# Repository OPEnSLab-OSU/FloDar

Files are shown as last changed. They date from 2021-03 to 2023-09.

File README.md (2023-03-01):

# FloDar | [Updates](https://github.com/OPEnSLab-OSU/OPEnS-Lab-Home/wiki/FloDar-updates) | [Wiki](https://github.com/OPEnSLab-OSU/OPEnS-Lab-Home/wiki/FloDar)

Project Lead: Cara Walter

This repository contains software, hardware, and documentation for FloDar.

See our [Wiki](https://github.com/OPEnSLab-OSU/OPEnS-Lab-Home/wiki/FloDar) for more information!

Project contact: Cara Walter (cara.walter@oregonstate.edu)

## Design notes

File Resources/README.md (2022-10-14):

# FloDar Resources

This directory is for holding diagrams, images, or other forms of documentation that may be referenced by our [Wiki](https://github.com/OPEnSLab-OSU/OPEnS-Lab-Home/wiki/FloDar) or elsewhere.

## System Diagram

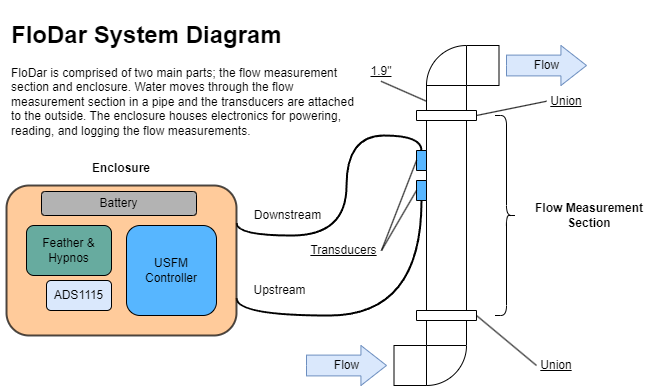
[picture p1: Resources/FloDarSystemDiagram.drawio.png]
FloDarSystemDiagram


## Circuit Diagram

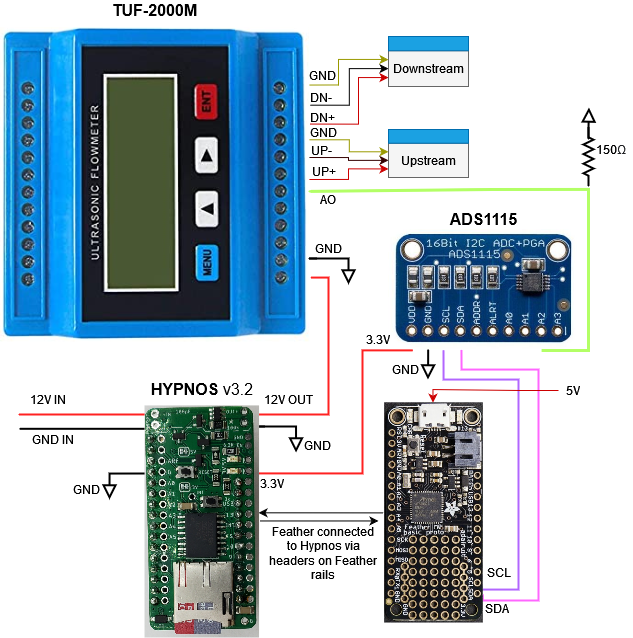
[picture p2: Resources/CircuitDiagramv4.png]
CircuitDiagram


## Black Box Diagram
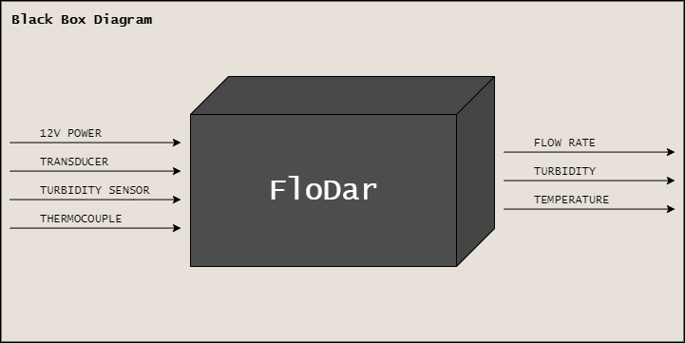
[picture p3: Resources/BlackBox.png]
Black Box Diagram


## FloDar Render
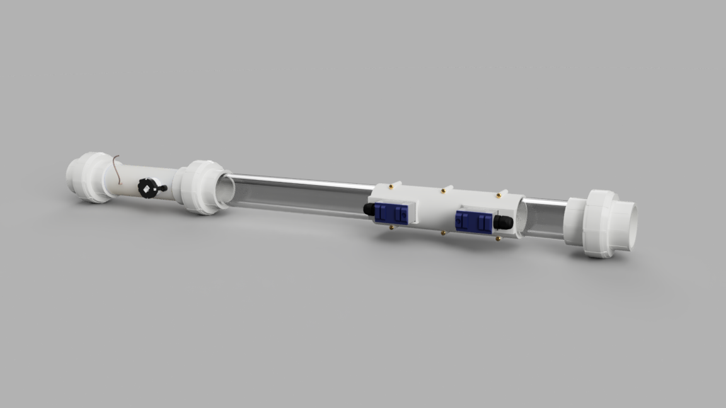
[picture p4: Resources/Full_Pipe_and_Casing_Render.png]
FloDar Render


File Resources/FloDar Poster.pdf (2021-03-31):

# FloDar

# Andrew Walker

1

# , Dexter Carpenter

1

# , Hadi Abdulameer Jasim Al-Agele

1

# , Cara Walter

2
,

# Dr. Chet Udell

2

# , Dr. John S Selker

2

1Openly Published Environmental Sensing Lab,

## 2Department of Biological & Ecological Engineering, Oregon State University

# PURPOSE

# tABSTRACT

- • Context/Purpose: The purpose of this experiment is to help remotely monitor water flow through collection pipes near roads and highways to identify factors contributing to landslides.
- • Methods: The three variables being collected for the detection of landslides are temperature, turbidity, and water flow rate. Sensors detecting these variables are inserted into a PVC structure that will be placed at the bottom of the current water collection system. All data will be recorded to an SD and eventually transmitted to the web using LoRa.
- • Results: The ultrasonic flowmeter used in the sensing system has show low accuracy (12% to 28% error) when the flow is below 5 LPM but high accuracy (7% to 1%) at flows higher than 7 LPM. The turbidity sensor has shown to have qualitative accuracy, not quantitative (NTU) accuracy. The system has only lasted 8 days in the field so far, but efforts are being made to improve its life.
- • Interpretation: The client is happy with the accuracy of the sensor and finds the sensitivity of the other sensors acceptable. Because the locations where these sensor systems will be implemented will be remote, the length the sensor can be active is very important. The team is working on adding a solar system to improve the life span.
- • Conclusion: Though life in the field should be improved, the low cost and accuracy of the system will already improve research on the subject.

Contact Information

Presenter: Andrew Walker & Dexter Carpenter (walkera6@oregonstate.edu, carpende@oregonstate.edu )

Lab Director: Chet Udell
(udellc@oregonstate.edu)

Website/Projects:
(http://www.open-sensing.org/)

This project would not have been possible without funding and insight given by the OSU Forestry Department Professor, Dr. Ben Leschinsky, and his graduate student, Mahrooz Abed. This funding was provided in connection with Oregon Department of Transportation, so the FloDar team is extremely grateful for the opportunity to receive these resources. All Professors in the OPEnS Lab have been instrumental in designing and testing the FloDar system, with Dr. Chet Udell providing the initial components, circuitry, and direction while Cara Walter, PE and Dr. John Selker have ensured all piping and flow parameters have been accounted for in the design. Though he is no longer working directly on the project, Hadi Abdulameer Jasim Al-Agele helped a great deal initializing the project, creating the prototype for the transducer collar and helping Andrew Walker become acclimated to the lab.
We would also be remiss if we did not thank the many lab members that gave advice and oversight while creating the many sub-designs throughout the project. Without the Loom Team, we would not have been able to make the software as easily or quickly; without Bao Nguyen, we would not have had to do much research to create the proper circuitry for the project; and without the support of the rest of the teams in the lab we would have missed essential feedback and new ideas that helped refine the project over time.

When creating the FloDar system, it was necessary to accommodate the collection piping within the field. To do so, a premade PVC pipe section was created with two sub-sections, one specifically for the ultrasonic flowmeter (USFM) and the other for the turbidity sensor and thermocouple. This design was made to ensure that any sub-section can be replaced if maintenance or repair is ever needed. The sections are connected using a PVC screw-on union to ease the process of set-up and replacement. To ensure all components were inserted and no water could escape a waterproof 2-part epoxy was used. Installing the transducers of the USFM can be tedious if only one technician is available, so a 3D printed collar has been created to quicken the process and increase the accuracy of transducer spacing distance.

# METHODS

# COMPONENT BREAKDOWN

All electronic components in the FloDar system are powered using the Talent Cell battery and recharged using a 10W solar panel and SunSaver controller. The thermocouple is attached to the MAX31856 for data collection and recording to the Feather M0 while the USFM and turbidity sensor data are recorded using the ADS1115 to improve accuracy. Because each sensor requires a different voltage supply, the OPEnS Hypnos board was selected as it has enough power supply rails to accommodate the project. The Hypnos board also improved the timing of the Feather M0 and allows recording to an SD card, which made its selection perfect for the project. All components are stored in a waterproof Pelican Case to ensure no damage occurs in the field. With proper construction, the researcher can easily take the connected pipe section into the field, insert it into the collection pipe, and place the Pelican case nearby after turning the sensor system on. They can then leave FloDar in the field and come check on it whenever they wish to collect data, taking the time to exchange batteries if necessary.

# RESULTS

# ACKNOWLEDGMENTS

DFRobot GRAVITY: ANALOG TURBIDITY SENSOR – Measuring Turbidity

TUF-2000M VTSYIQI Ultrasonic Flow Meter – Measuring Flow

Thermocouple Amplifier MAX31856 & Steel Tip Type-K – Measuring Temperature

OPEnS Hypnos Board – Timing, Power Supply Controller, SD Card & Recording

Arduino LoRa Feather M0 – Microcontroller TalentCell Rechargeable 12V 6000mAh/5V 12000mAh – Power Supply

Newpowa 20W Monocrystalline Solar Panel & Morningstar SunSaver Controller – Battery Recharge

# CONCLUSIONS: FUTURE DIRECTION

As climate change progresses and extreme weather events begin to occur more frequently a better understanding of the effect precipitation can have on landslides is necessary. It is hoped that the FloDar system can help researchers and government organizations record data from various locations, especially remote areas, that will allow for this understanding. So far, the system has shown great promise in its ability to accurately measure flow and give some insight to the turbidity and temperature within the collection system. Though more long-term testing is necessary and there is room for improvement for the lifetime of FloDar out in the field, we look forward to seeing how we can make the project better in the coming months.

Testing Methodology:

1. Turn on the pump at 20% of maximum flow rate
2. Wait until all bubbles and air gaps have been removed from system
3. If some gaps will not leave the system, turn the flow rate up to 40% until they leave and then turn back down to 20%
4. Place your 500mL volumetric measuring equipment into the collection basin
5. Turn on USFM
6. Reset your stopwatch to zero
7. With one hand, place outflow tube over your 500mL volumetric measuring equipment, starting the timer immediately
8. Wait until 500mL has been reached then immediately stop the stopwatch
9. Record trial
10. Look at reading on USFM, record trial
11. Turn off USFM
12. Empty 500mL volumetric measuring equipment
13. Repeat steps 3-11 until you have at least 5 trials for flow rate
14. Repeat steps 3-12 for 30%, 40%, 50%, & 60%

# TESTING

To ensure the Ultrasonic Flowmeter selected for this system would provide accurate results, an experiment was devised to test the percent error in relation to the flow rate within the Calibration System mentioned below. The sensor's technical manual describes a limit to the accuracy associated with low flows, which was also seen in the experiment. However, the experiment also showed that as the flow rate increased the error rate decreased for most trials. Because mean error for the error rate increased between the final two flow settings, the experiment may need to be conducted again with higher flows to see if the error rate is parabolic or if the error rate truly shows a exponential approaching zero.

It has been documented that intense rainfall in areas with a high susceptibility to landslides can trigger the occurrence of landslides. (Hughes and Schulz, 2020) With climate change leading to more extreme weather events it is beneficial to have an early warning system when such extreme events are occurring in such areas. This system -combined with other geological data, such as a location’s soil properties and terrain map -can allow for a better understanding of exactly what factors cause a landslide event to occur and help government organizations, such as ODOT, to take measures in rerouting traffic or restoring roads. It is with these premises in mind that the FloDar system has been created. When FloDar is implemented in drainage pipes at study areas, researchers can better understand how water flow, temperature, and turbidity within the collected water can affect the occurrence of a landslide. FloDar uses sensors specifically tailored to these variables to record the sensor values in time-intervals of 15 minutes, and eventually be able to transmit this data from remote locations using LoRa. This data can help researchers and government organizations to develop a monitoring database for various locations that may work as an early detection system, alerting authorities of the specific time and the current state of the area when an event occurs.

Figure 1: New Transducer Holder

Figure 2: Example of Installed Transducers

Figure 3: Electrical Components and Circuit

Figure 4: System Design

Figure 5: Graph of Accuracy vs. Flow Rate

Table 1: REsults of Accuracy vs. Flow Rate Test

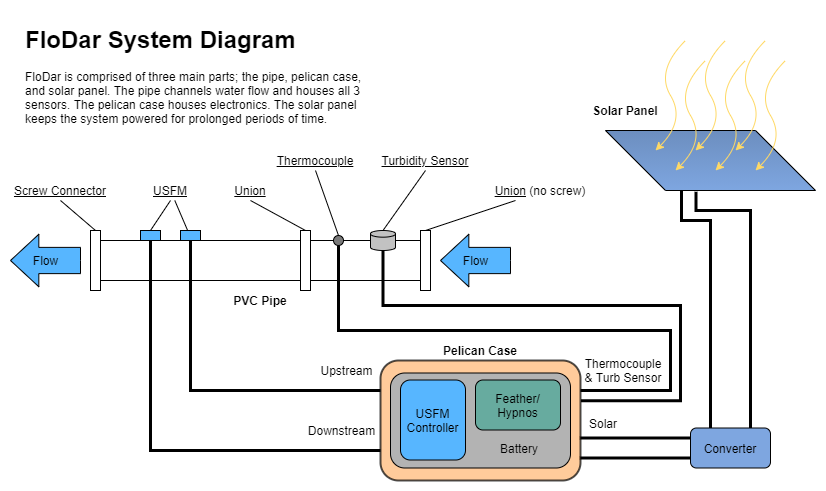
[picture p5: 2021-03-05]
Resources/FloDarSystemDiagram.png

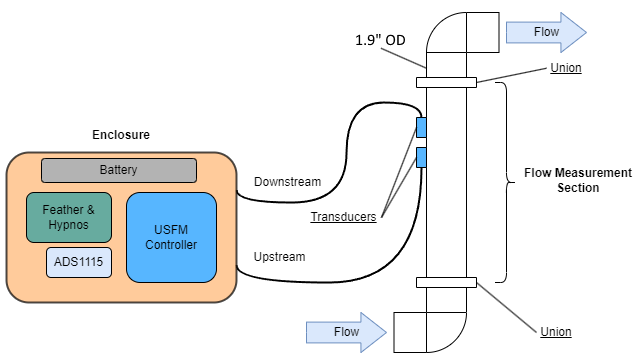
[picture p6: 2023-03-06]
Resources/FloDarSystemDiagram_USFM_only.png

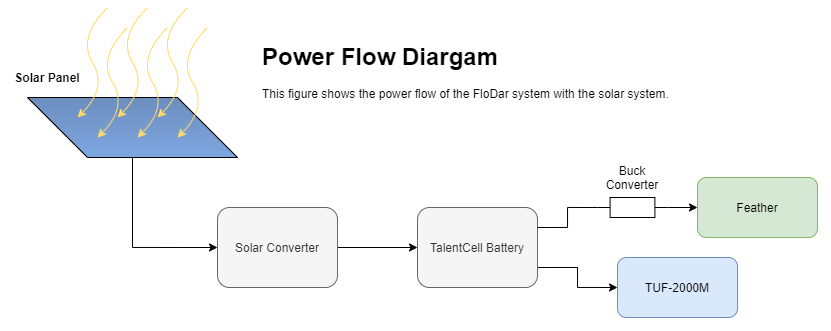
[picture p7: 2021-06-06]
Resources/Power Budget.png

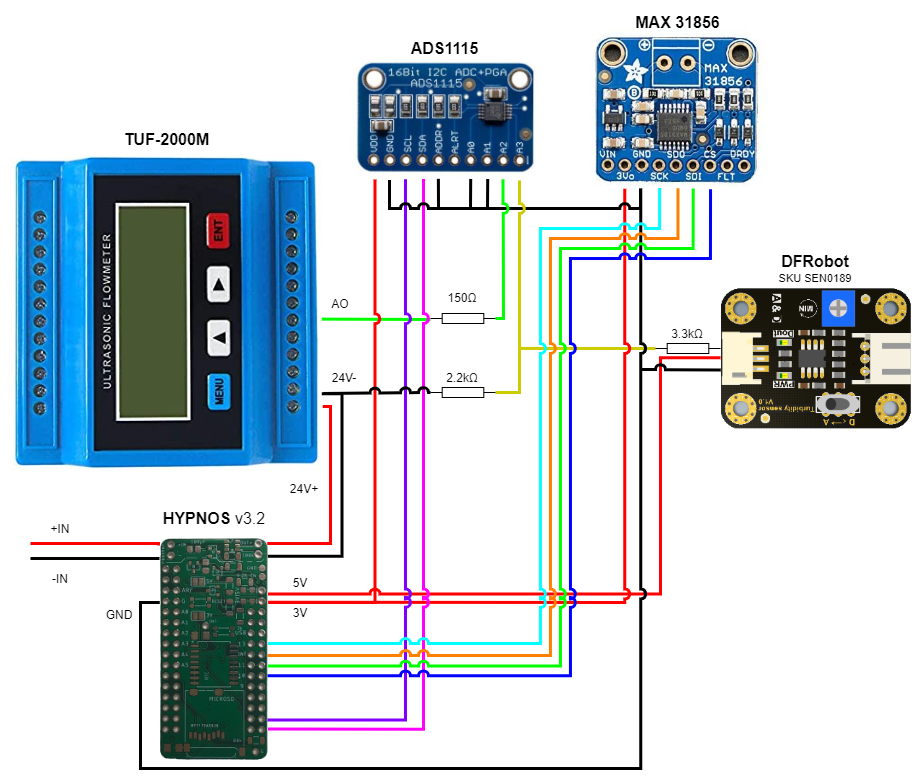
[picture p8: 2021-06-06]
Resources/CircuitDiagram_Transp.png

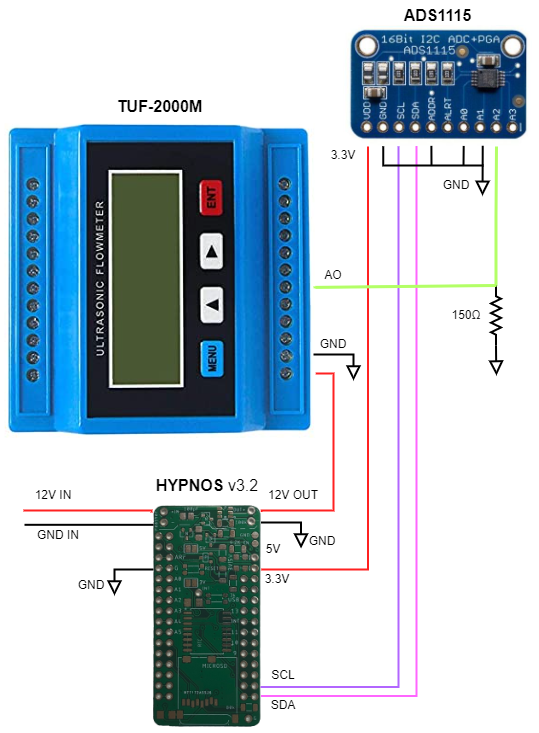
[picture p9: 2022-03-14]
Resources/CircuitDiagram.png

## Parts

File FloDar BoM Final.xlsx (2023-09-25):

Designator | Component | Qty. | Cost per Unit | Total Cost | Source of Materials | Notes
Mechanical Components
Pelican Case | 1150 Pelican Case | 1 | $49.95 | $49.95 | B&H Photo (https://www.bhphotovideo.com/c/product/106483-REG/Pelican_1150_000_120_1150_Case_with_Foam.html)
Structure | Acryllic 1/8" x 12" x 12' | 1 | $4.99 | $4.99 | Grainger (https://www.grainger.com/product/GRAINGER-APPROVED-Plastic-Sheet-0-125-in-Thick-1UNK4?opr=APPD&analytics=altItems_1UNK8&position=1) | Each design uses 8.27" x 5.81"
Cable Gland | PG7 Plastic Waterproof Cable Gland Connectors | 2 | $0.45 | $0.90 | Amazon (https://www.amazon.com/Lokman-Plastic-Waterproof-Adjustable-Connectors/dp/B06Y5HGYK2) | Pack of 20
Drill bit | Multidiameter Drill Bit | 1 | $21.85 | $21.85 | McMaster (https://www.mcmaster.com/8841A21/)
12mm M3 Screw | 18-8 Stainless Steel Socket Head Screw | 4 | $0.06 | $0.24 | McMaster (https://www.mcmaster.com/91292A114/) | Pack of 100
M3 Jam Nut | Steel Thin Hex Nut | 8 | $0.04 | $0.34 | McMaster (https://www.mcmaster.com/90695A033/) | Pack of 100
Velcro | Velcro 3/4 in x 30 ft Roll | 25 | $0.01 | $0.27 | Amazon (https://www.amazon.com/gp/product/B09QH265VR/ref=ppx_yo_dt_b_search_asin_title?ie=UTF8&th=1) | ~25 cm needed for each
PVC Pipe | 2.5' 1.5" schedule 40 PVC | 1 | $18.43 | $18.43 | McMaster (https://www.mcmaster.com/49035K112/) | Minimum order length 10'
Marine Epoxy | Loctite Epoxy Marine, 0.85 fl oz | 1 | $8.50 | $8.50 | Amazon (https://www.amazon.com/Loctite-1919324-0-85-Fluid-Syringe-1405604/dp/B00KH62K50?cv_ct_cx=marine+epoxy&sbo=RZvfv%2F%2FHxDF%2BO5021pAnSA%3D%3D)
Electrical Components
Feather | Adafruit Feather M0 Basic Proto | 1 | $19.95 | $19.95 | Adafruit (https://www.adafruit.com/product/2772)
Hypnos | Hypnos V3.2 or V3.3 | 1 | $27.00 | $27.00 | OPEnS
2 pin JST right angle socket | 2 pin JST XH right angle socket | 2 | $0.19 | $0.38 | Digi-key (https://www.digikey.com/en/products/detail/jst-sales-america-inc/S2B-XH-A-1-LF-SN/9961922?s=N4IgTCBcDaICwFYEFo5jANmQOQCIgF0BfIA)
Male headers | 28 for Hypnos | 1 | $0.50 | $0.50 | Adafruit (https://www.adafruit.com/product/3002)
Female headers | 10 for ADS1115, 30 for Hypnos | 1 | $2.95 | $2.95 | Adafruit (https://www.adafruit.com/product/598)
Breakout Board | FloDar Breakout Board | 1 | $3.87 | $3.87 | OPEnS | Minimum order of 3
Resistor | SAMD 150 Ohm Resistor | 1 | $2.12 | $2.12 | Digi-key (https://www.digikey.com/en/products/detail/stackpole-electronics-inc/RNCF1206TKY150R/9919719)
Tripler | FeatherWing Tripler Mini Kit | 1 | $8.50 | $8.50 | Adafruit (https://www.adafruit.com/product/3417)
ADS1115 | ADS1115 16-Bit ADC | 1 | $14.95 | $14.95 | Adafruit (https://www.adafruit.com/product/1085)
SD Card | SanDisk 32GB microSDHC Memory Card with SD Adapter | 1 | $7.95 | $7.95 | B&H Photo (https://www.bhphotovideo.com/c/product/1638656-REG/sandisk_sdsqunr_032_gn3ma_32gb_ultra_uhs_i_microsd.html)
Coin Cell | CR1220 | 1 | $0.88 | $0.88 | Digi-key (https://www.digikey.com/en/products/detail/murata-electronics/CR1220/9558419)
Cable Connector | Waterproof Polarized 4-Wire Cable Set | 2 | $2.50 | $5.00 | Adafruit (https://www.adafruit.com/product/744)
USB Cable | Micro USB Cable | 1 | $1.60 | $1.60 | Amazon (https://www.amazon.com/Spater-Micro-USB-Cable-Motorola/dp/B01FSYBQ9Q) | Pack of 5
3-pin JST plug cables and sockets | 3 PIN JST XH plug 200mm 26 AWG cable, socket | 1 | $0.75 | $0.75 | Amazon (https://www.amazon.com/2-54MM-Female-Double-Connector-Wires/dp/B07XNWD58H?s=hi) | Pack of 20
2-pin JST cables | 22 AWG 2 Pin JST XH2.54 Connector Plug | 2 | $0.50 | $1.00 | Amazon (https://www.amazon.com/mxuteuk-XH2-54-Connector-Female-JST-XH2-54/dp/B083HWDPSV?s=hi) | Pack of 20, 10 usable
Battery | TalentCell Rechargeable 12V Lithium Ion Battery | 1 | $39.99 | $39.99 | Amazon (https://www.amazon.com/TalentCell-Rechargeable-12000mAh-Multi-led-indicator/dp/B00ME3ZH7C)
DC Power Jack | DC Power Jack Plug Adapter | 1 | $1.00 | $1.00 | Amazon (https://www.amazon.com/DAYKIT-Female-2-1x5-5MM-Adapter-Connector/dp/B01J1WZENK) | Pack of 10
Flow Meter
USFM | TUF-2000M | 1 | $253.00 | $253.00 | Amazon (https://www.amazon.com/VTSYIQI-TUF-2000M-TS-2-Ultrasonic-Waterproof-DN15-100mm/dp/B07JNR2HGW)
Transducer | TS-2 Pair | 1 | (included) | -
Transducer Cable | Transducer Cable | 5 meters | (included) | -
Hose Clamps | Hose Clamps | 2 | (included) | -
Heat Shrink | Heat Shrink | 8 | (included) | - |  | 2x Red 2x Blue 4x Black small
Spades | Fork Spade U-Type Connectors | 6 | (included) | -
Large black heat shrink | 1/4" 3:1 adhesive lined heat shrink | 5 | $0.05 | $0.25 | Amazon (https://www.amazon.com/gp/product/B0919J58MH/ref=ppx_yo_dt_b_search_asin_title?ie=UTF8&th=1) | 20 ft, each cable needs 2.5"
Solder seal connectors | Marine grade solder seal connectors 18-22 gauge | 6 | $0.20 | $1.20 | Amazon (https://www.amazon.com/Connectors-Haisstronica-Electrical-Waterproof-Automotive/dp/B07C3MKM3K?hvadid=259499196890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) | Pack of 50, 1.5" long
Silicon Lubricant | Dow Corning 111 O-Ring Silicone Lubricant | 1 | $7.95 | $7.95 | Amazon (https://www.amazon.com/Dow-Corning-Molykote-Oring-Lubricant/dp/B075Y5DCY9?s=industrial)

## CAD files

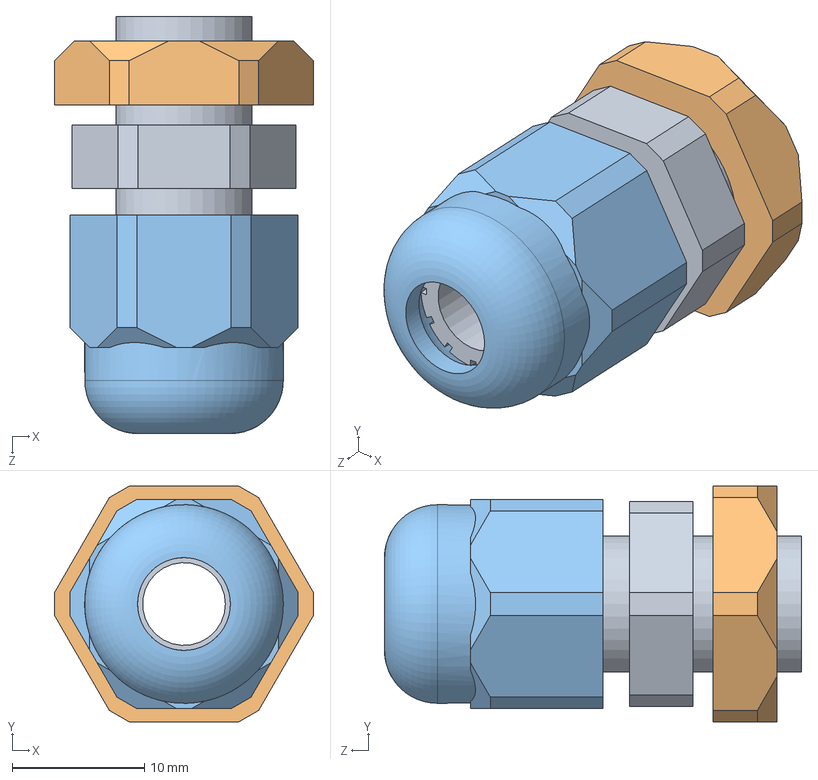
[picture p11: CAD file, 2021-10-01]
CAD/Components/PG7-CableGland/PG7-CableGland.SLDASM
19.6 x 17.8 x 31.5 mm
PG7-CableGland-Body
PG7-CableGland-Back
PG7-CableGland-Cap

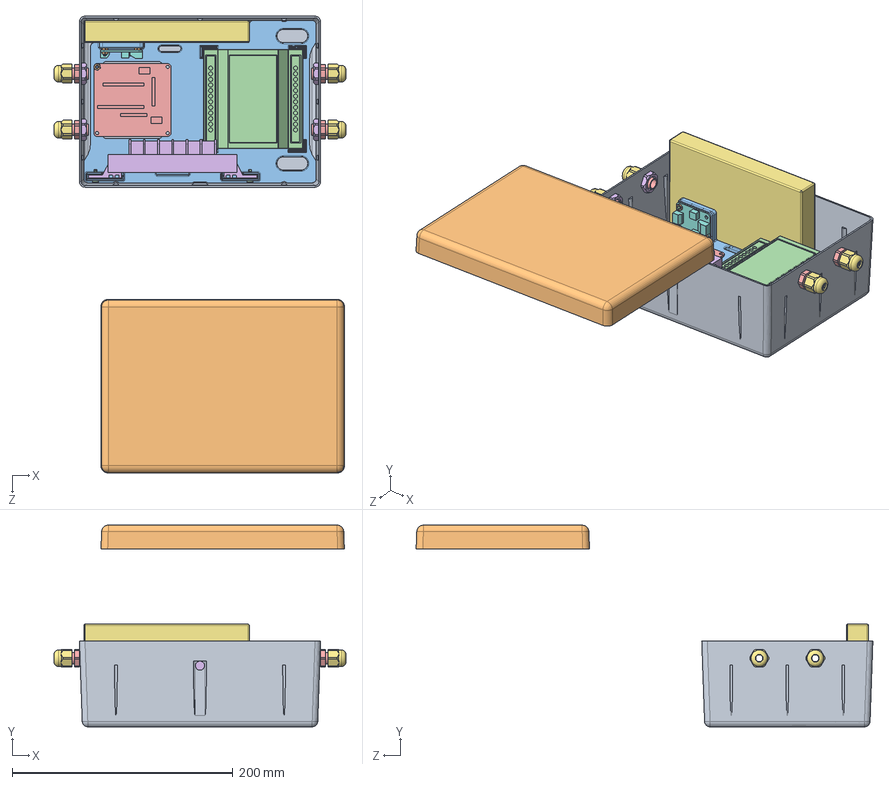
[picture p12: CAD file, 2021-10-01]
CAD/Pelican Structure/Pelican Structure.SLDASM
264.8 x 182.9 x 414.2 mm
1150 new case Base
Pelican Structure
TUF-2000M
PowerDistBoard
SunSaver-10L (V2)
UB1220-T
DFRobot_Turbidity-Sensor
95495K511_Adhesive-Back Bumpers x 4
90695A033_Steel Thin Hex Nut x 6
91292A114_TYPE 18-8 SS SOCKET HEAD CAP SCREW
M3 Low-Profile Socket Head Screws x 4
PG7-CableGland-Body x 4
PG7-CableGland-Back x 4
PG7-CableGland-Cap x 4

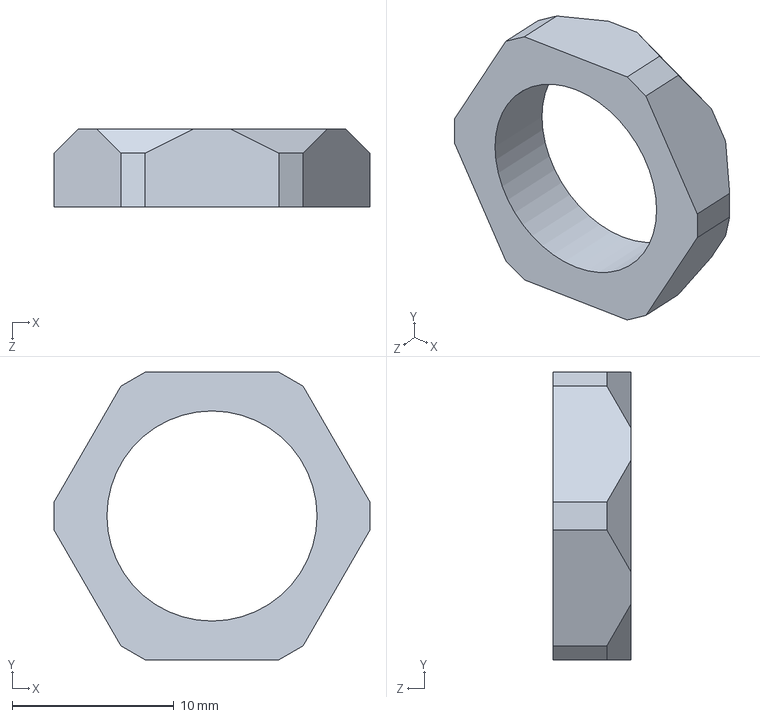
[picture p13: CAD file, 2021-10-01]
CAD/Components/PG7-CableGland/PG7-CableGland-Back.SLDPRT
19.6 x 17.8 x 4.84 mm

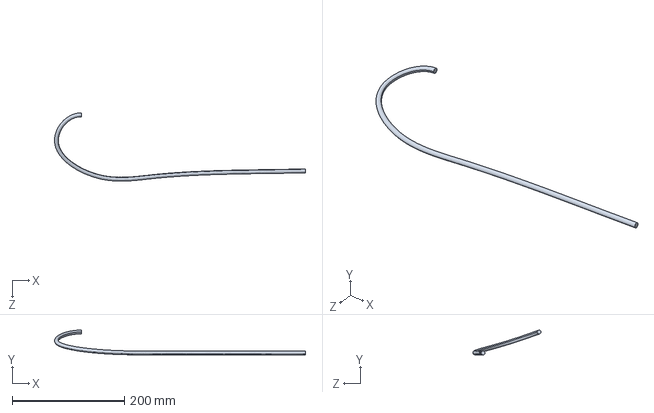
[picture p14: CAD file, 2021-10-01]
CAD/Components/STEP/Up-Cable.STEP
447.9 x 44.4 x 121.9 mm

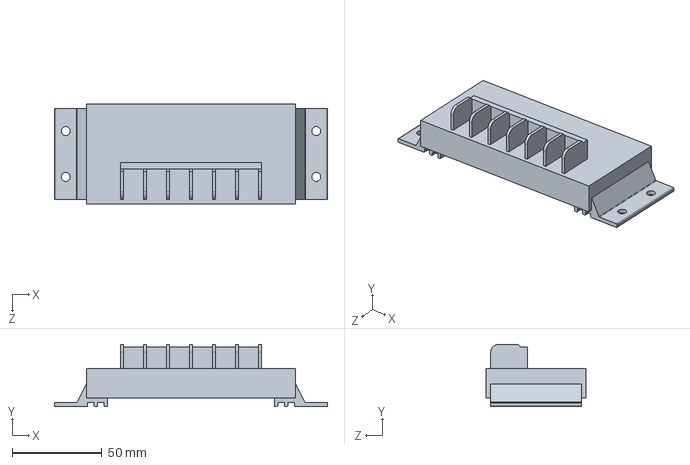
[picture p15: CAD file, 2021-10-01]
CAD/Components/SunSaver-10L (V2).SLDPRT
152.5 x 34.7 x 55.6 mm

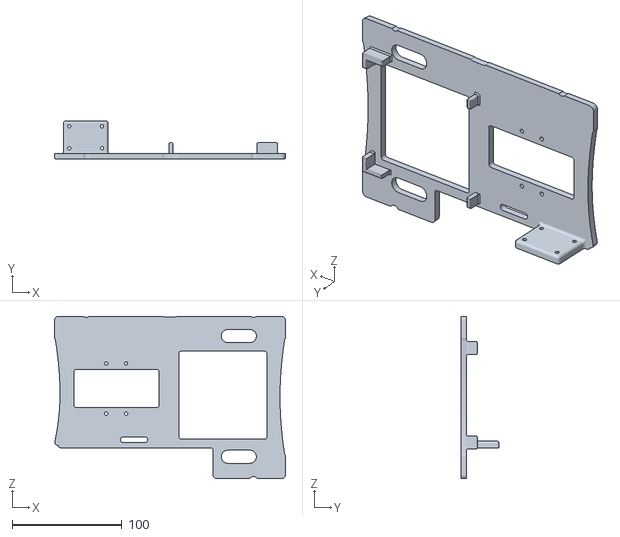
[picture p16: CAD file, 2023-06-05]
CAD/Pelican Structure/FloDar_insert.stl
210.5 x 35.0 x 148.0

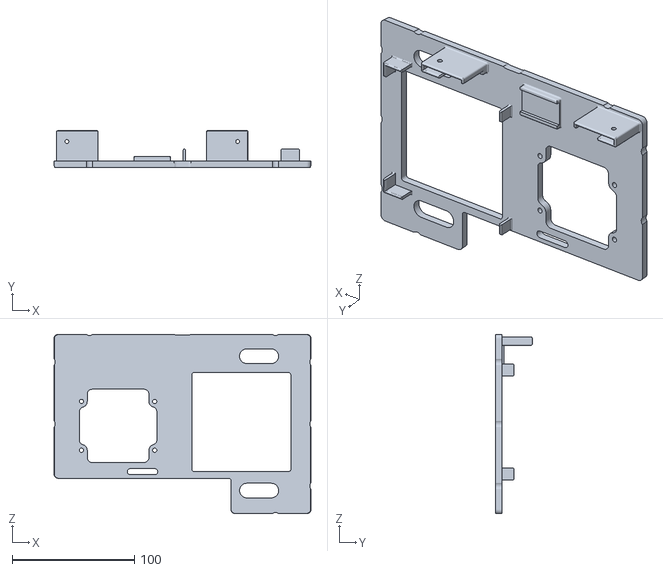
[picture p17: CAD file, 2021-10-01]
CAD/Pelican Structure/STL/Pelican_Structure_Print_V2.STL
210.5 x 30.0 x 147.0

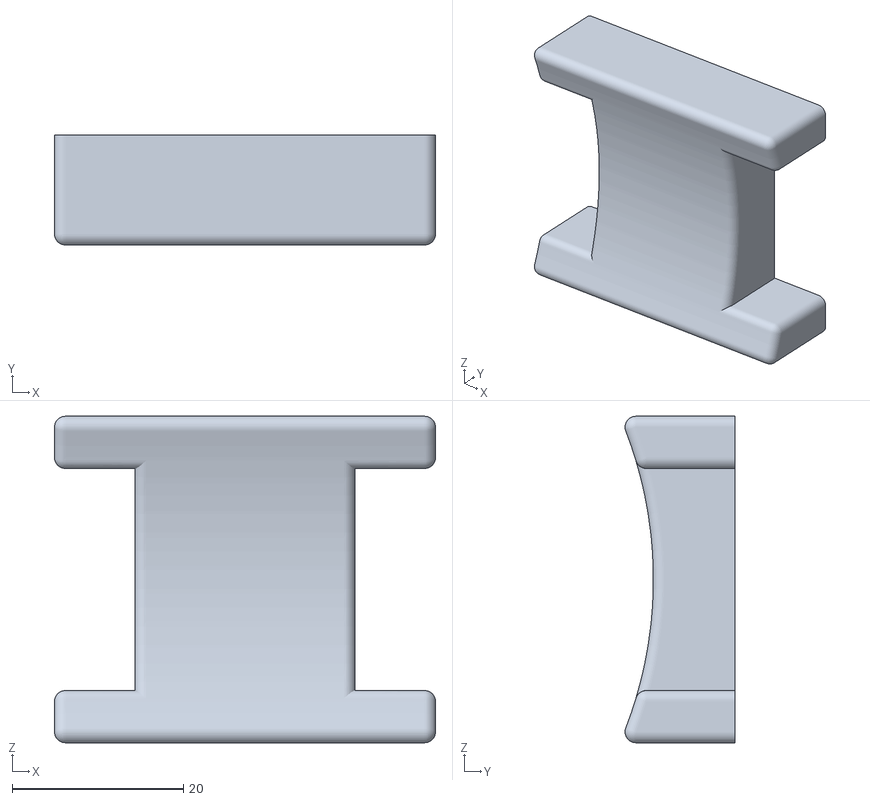
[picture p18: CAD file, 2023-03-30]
CAD/Transducer_1-5_Spacer.STL
44.5 x 12.8 x 38.1

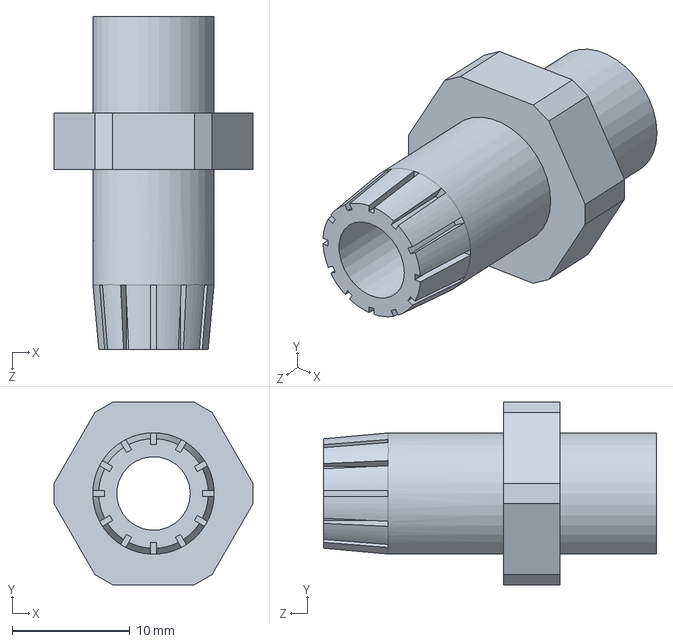
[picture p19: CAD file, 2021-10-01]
CAD/Components/PG7-CableGland/PG7-CableGland-Body.SLDPRT
16.9 x 15.5 x 28.3 mm

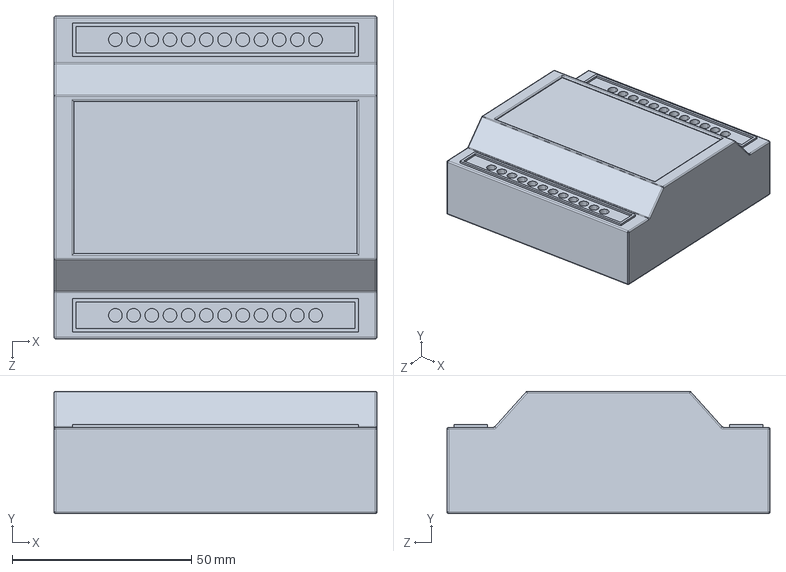
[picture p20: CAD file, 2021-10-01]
CAD/Components/STEP/TUF-2000M.STEP
90.2 x 34.2 x 90.2 mm

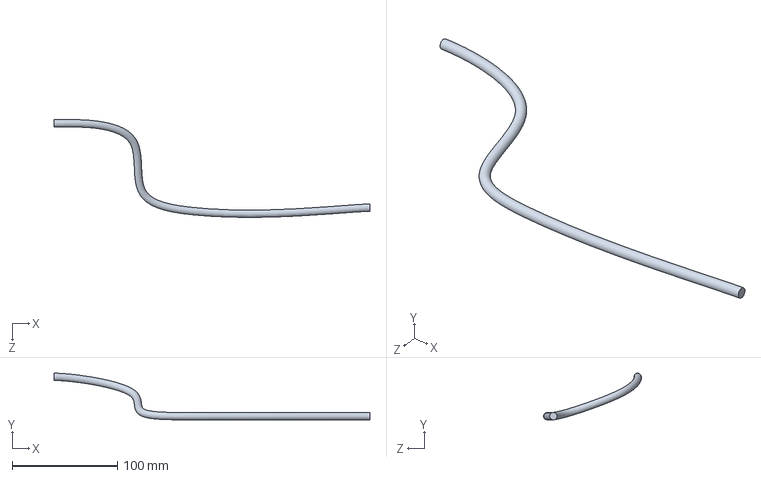
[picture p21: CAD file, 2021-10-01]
CAD/Components/Transducer Cables/Down-Cable.SLDPRT
300.1 x 44.4 x 92.9 mm

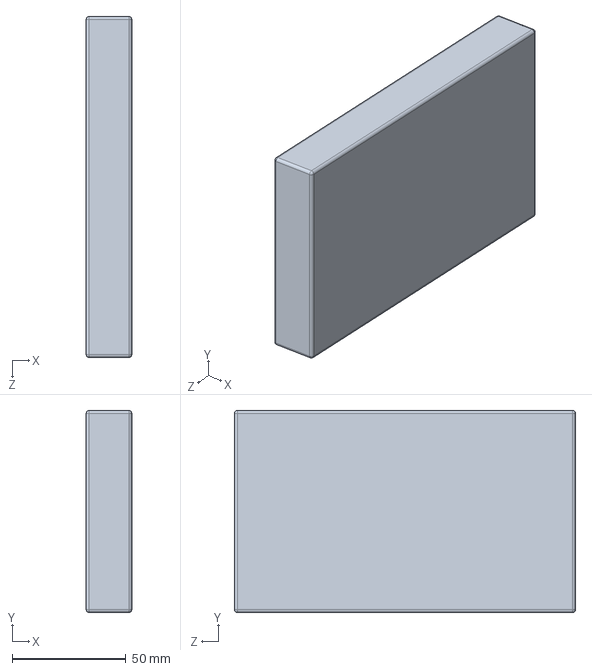
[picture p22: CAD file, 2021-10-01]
CAD/Components/UB1220-T.SLDPRT
20.1 x 88.9 x 150.1 mm

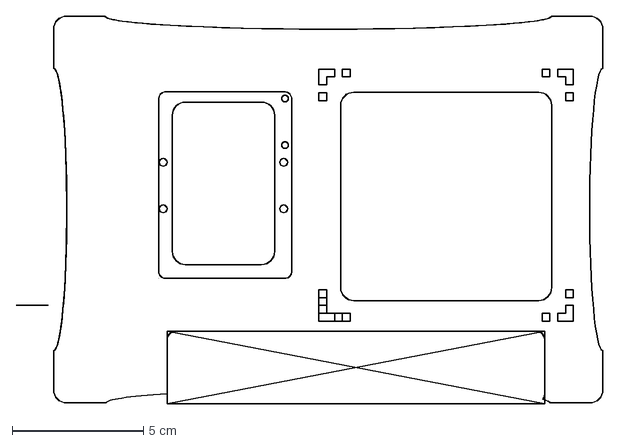
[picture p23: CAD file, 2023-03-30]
CAD/Pelican Structure/Flodar_Laser_Cut_Insert_Batch4_final_4_22_22 v4.dxf
22.4 x 14.8 cm

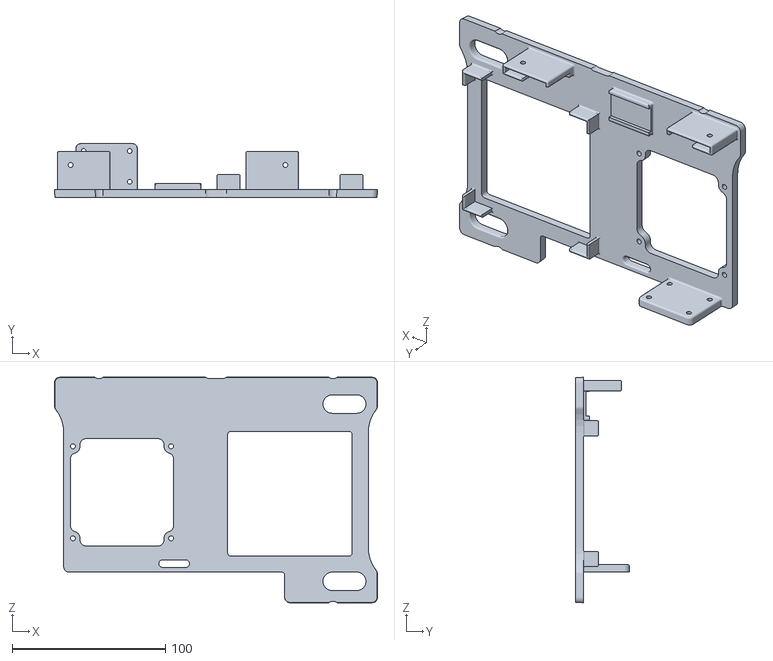
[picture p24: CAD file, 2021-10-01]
CAD/Pelican Structure/STL/Pelican_Structure_Print_V3.STL
210.5 x 35.0 x 147.0

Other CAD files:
CAD/Components/Transducer Cables/Up-Cable.SLDPRT
CAD/Components/PG7-CableGland/PG7-CableGland-Cap.SLDPRT
CAD/Components/STEP/Down-Cable.STEP
CAD/Pelican Structure/FloDar_Insert_Solar_Turbidity_Print.stl
CAD/Components/1150 new case Base.SLDPRT
CAD/Components/1150 new case top.SLDPRT
CAD/Components/7310K11_Plastic Submersible Cord Grip.SLDPRT
CAD/Components/90695A033_Steel Thin Hex Nut.SLDPRT
CAD/Components/91292A114_TYPE 18-8 SS SOCKET HEAD CAP SCREW.SLDPRT
CAD/Components/95495K511_Adhesive-Back Bumpers.SLDPRT
CAD/Components/DFRobot_Turbidity-Sensor.SLDPRT
CAD/Components/M25 Hex Jam Nut.SLDPRT
CAD/Components/M25 Socket 12mm Screw.SLDPRT
CAD/Components/M3 Low-Profile Socket Head Screws.SLDPRT
CAD/Components/PS-1223.SLDPRT
CAD/Components/Part1.SLDPRT
CAD/Components/PowerDistBoard.SLDPRT
CAD/Components/STEP/DFRobot_Turbidity-Sensor.step
CAD/Components/STEP/SunSaver-10L.step
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

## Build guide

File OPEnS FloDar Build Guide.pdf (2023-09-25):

FloDar: An Inline Flow Meter for Landslide Drains

Authors: Cara Waltera,b, Dexter Carpentera

, Duane Knappa
,

Affiliations

a. OPEnS Lab, Oregon State University, Corvallis, OR, United States
b. Department of Biological & Ecological Engineering, Oregon State University, Corvallis, OR, United States

### 1. Overview


Figure 1: FloDar System Diagram

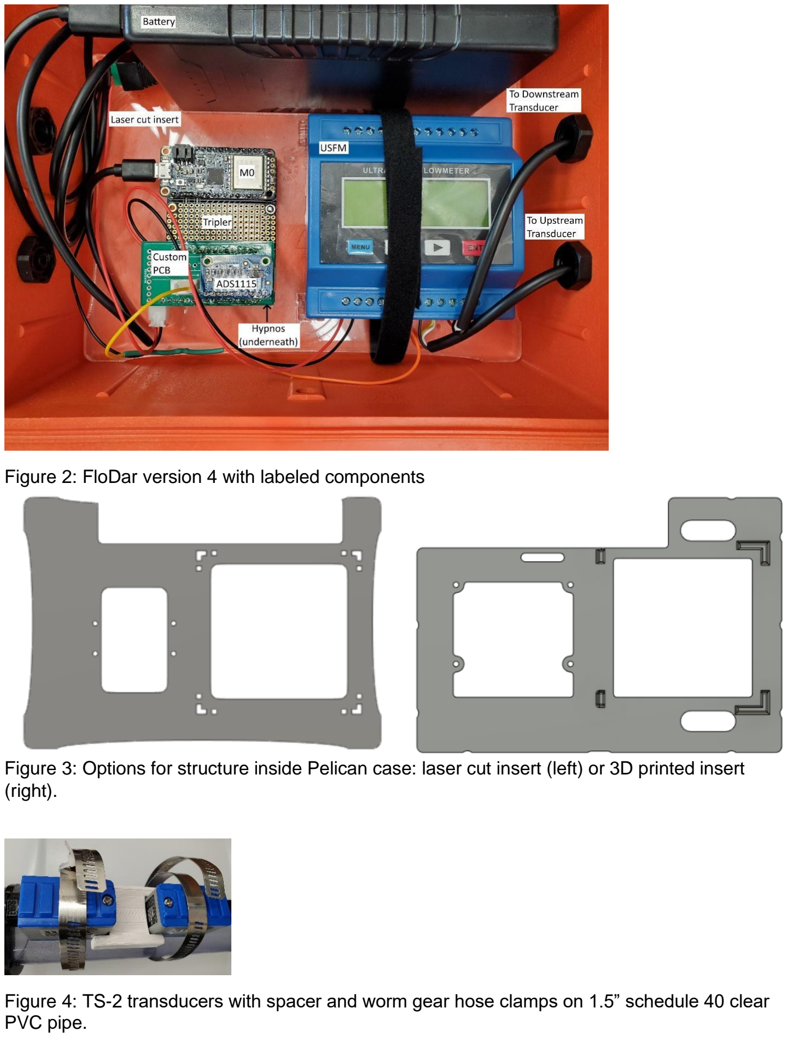
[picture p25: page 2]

Figure 2: FloDar version 4 with labeled components

Figure 3: Options for structure inside Pelican case: laser cut insert (left) or 3D printed insert (right).

Figure 4: TS-2 transducers with spacer and worm gear hose clamps on 1.5” schedule 40 clear PVC pipe.

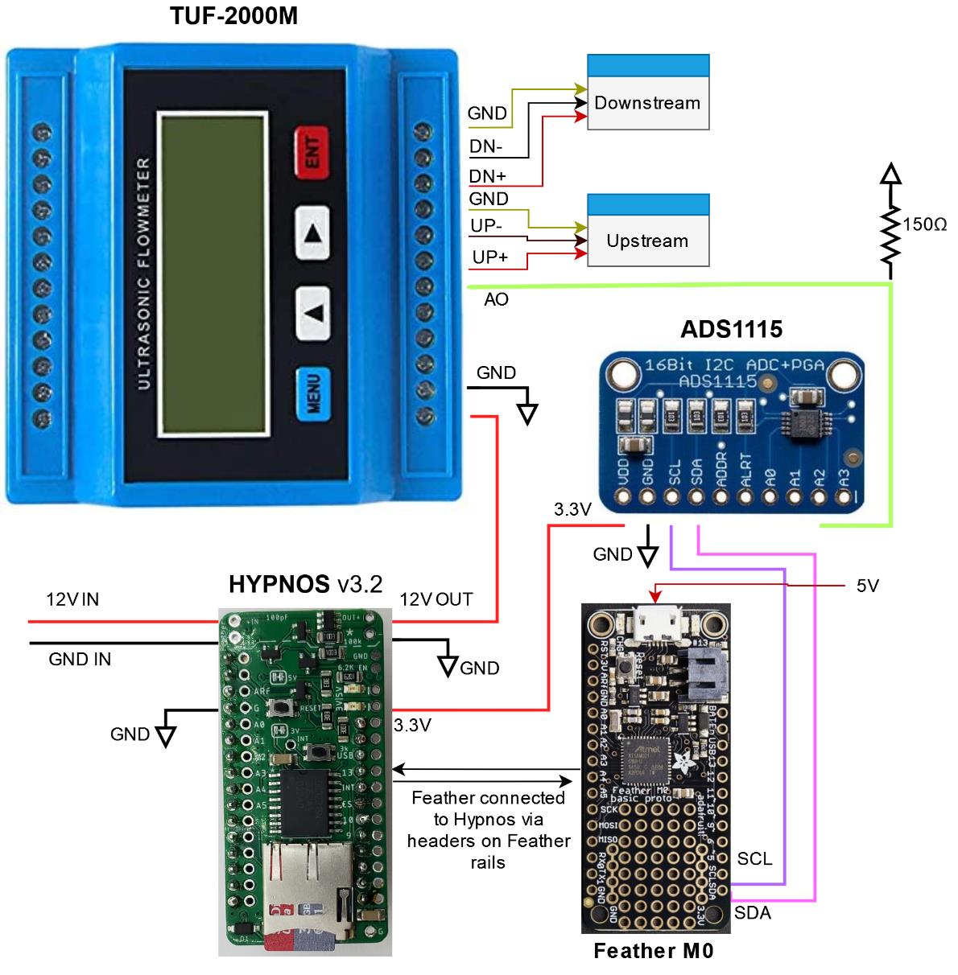
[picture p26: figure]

Figure 5: Circuit diagram of major electrical components with connections

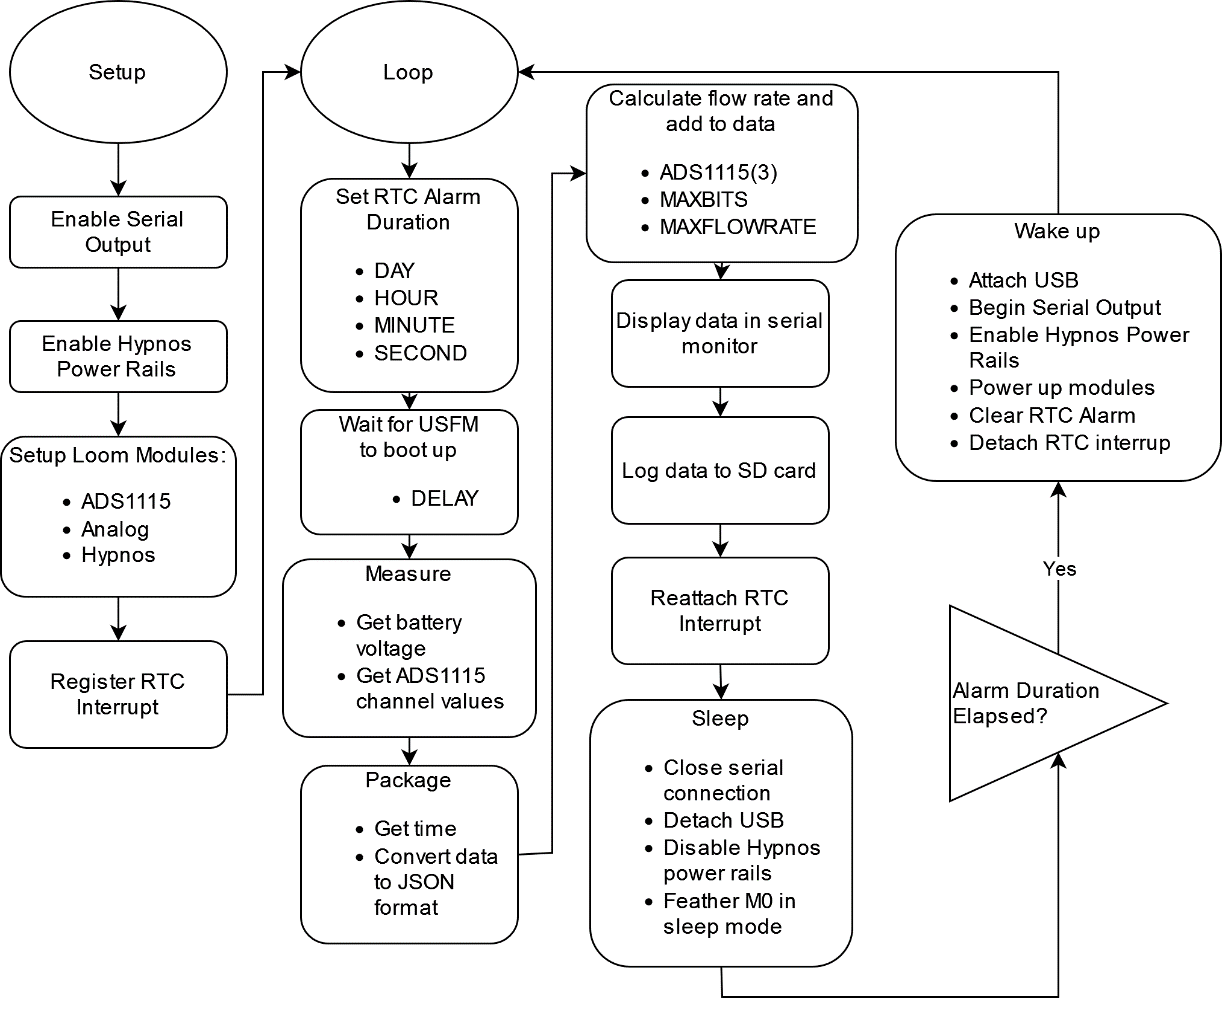
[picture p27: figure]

Figure 6: FloDar Loom 4 Software Diagram

### 2. Design Files

Design Filename | File Type | Description | Source
Pelican Insert Laser Cut | DXF | Acrylic insert option for holding components in place. | Github (https://github.com/OPEnSLab-OSU/FloDar/blob/main/CAD/Pelican%20Structure/Flodar_Laser_Cut_Insert_Batch4_final_4_22_22%20v4.dxf)
Pelican Insert 3D Print | STL | ASA insert option for holding components in place. | Github (https://github.com/OPEnSLab-OSU/FloDar/blob/main/CAD/Pelican%20Structure/Pelican_Structure_Print.stl)
Transducer Spacer | STL | ASA spacer for ensuring exact transducer separation for V method installation on 1.5” schedule 40 pipe. | Github (https://github.com/OPEnSLab-OSU/FloDar/blob/main/CAD/Transducer_1-5_Spacer.STL)
Breakout Board | Gerber | Custom PCB for connecting electrical components. | Github (https://github.com/OPEnSLab-OSU/FloDar/blob/main/Boards/FLODAR_V4_2021-06-29.zip)
FloDar_Field_Lo om4_1 | ino | Arduino code for operating system. | Github (https://github.com/OPEnSLab-OSU/FloDar/blob/main/Software/Loom%204/FloDar_Field_Loom4_1/FloDar_Field_Loom4_1.ino)

### 3. Bill of Materials

### 3.1 Mechanical Components

Designator | Component | Qty. | Cost per Unit | Total Cost | Source of Materials | Notes
Pelican Case | 1150 Pelican Case | 1 | $49.95 | $49.95 | B&H Photo (https://www.bhphotovideo.com/c/product/106483-REG/Pelican_1150_000_120_1150_Case_with_Foam.html)
Structure | Acryllic 1/8" x 12" x 12' | 1 | $4.99 | $4.99 | Grainger (https://www.grainger.com/product/GRAINGER-APPROVED-Plastic-Sheet-0-125-in-Thick-1UNK4?opr=APPD&analytics=altItems_1UNK8&position=1) | Each design uses 8.27" x 5.81"
Cable Gland | PG7 Plastic Waterproof Cable Gland Connectors | 2 | $0.45 | $0.90 | Amazon (https://www.amazon.com/Lokman-Plastic-Waterproof-Adjustable-Connectors/dp/B06Y5HGYK2) | Pack of 20
Drill bit | Multidiameter Drill Bit | 1 | $21.85 | $21.85 | McMaster (https://www.mcmaster.com/8841A21/)
12mm M3 Screw | 18-8 Stainless Steel Socket Head Screw | 4 | $0.06 | $0.24 | McMaster (https://www.mcmaster.com/91292A114/) | Pack of 100
M3 Jam Nut | Steel Thin Hex Nut | 8 | $0.04 | $0.34 | McMaster (https://www.mcmaster.com/90695A033/) | Pack of 100
Velcro | Velcro 3/4 in x 30 ft Roll | 25 | $0.01 | $0.27 | Amazon (https://www.amazon.com/gp/product/B09QH265VR/ref=ppx_yo_dt_b_search_asin_title?ie=UTF8&th=1) | ~25 cm needed for each
PVC Pipe | 2.5' 1.5" schedule 40 PVC | 1 | $18.43 | $18.43 | McMaster (https://www.mcmaster.com/49035K112/) | Minimum order length 10'
Marine Epoxy | Loctite Epoxy Marine, 0.85 fl oz | 1 | $8.50 | $8.50 | Amazon (https://www.amazon.com/Loctite-1919324-0-85-Fluid-Syringe-1405604/dp/B00KH62K50?cv_ct_cx=marine+epoxy&sbo=RZvfv%2F%2FHxDF%2BO5021pAnSA%3D%3D)

### 3.2 Electrical Components

Designator | Component | Qty. | Cost per Unit | Total Cost | Source of Materials | Notes
Feather | Adafruit Feather M0 Basic Proto | 1 | $19.95 | $19.95 | Adafruit (https://www.adafruit.com/product/2772)
Hypnos | Hypnos V3.2 or V3.3 | 1 | $27.00 | $27.00 | OPEnS
2 pin JST right angle socket | 2 pin JST XH right angle socket | 2 | $0.19 | $0.38 | Digi-key (https://www.digikey.com/en/products/detail/jst-sales-america-inc/S2B-XH-A-1-LF-SN/9961922?s=N4IgTCBcDaICwFYEFo5jANmQOQCIgF0BfIA)
Male headers | 28 for Hypnos | 1 | $0.50 | $0.50 | Adafruit (https://www.adafruit.com/product/3002)
Female headers | 10 for ADS1115, 30 for Hypnos | 1 | $2.95 | $2.95 | Adafruit (https://www.adafruit.com/product/598)
Breakout Board | FloDar Breakout Board | 1 | $3.87 | $3.87 | OPEnS | Minimum order of 3
Resistor | SAMD 150 Ohm Resistor | 1 | $2.12 | $2.12 | Digi-key (https://www.digikey.com/en/products/detail/stackpole-electronics-inc/RNCF1206TKY150R/9919719)
Tripler | FeatherWing Tripler Mini Kit | 1 | $8.50 | $8.50 | Adafruit (https://www.adafruit.com/product/3417)
ADS1115 | ADS1115 16-Bit ADC | 1 | $14.95 | $14.95 | Adafruit (https://www.adafruit.com/product/1085)
SD Card | SanDisk 32GB microSDHC Memory Card with SD Adapter | 1 | $7.95 | $7.95 | B&H Photo (https://www.bhphotovideo.com/c/product/1638656-REG/sandisk_sdsqunr_032_gn3ma_32gb_ultra_uhs_i_microsd.html)
Coin Cell | CR1220 | 1 | $0.88 | $0.88 | Digi-key (https://www.digikey.com/en/products/detail/murata-electronics/CR1220/9558419)

Cable Connector | Waterproof Polarized 4-Wire Cable Set | 2 | $2.50 | $5.00 | Adafruit (https://www.adafruit.com/product/744)
USB Cable | Micro USB Cable | 1 | $1.60 | $1.60 | Amazon (https://www.amazon.com/Spater-Micro-USB-Cable-Motorola/dp/B01FSYBQ9Q) | Pack of 5
3-pin JST plug cables and sockets | 3 PIN JST XH plug 200mm 26 AWG cable, socket | 1 | $0.75 | $0.75 | Amazon (https://www.amazon.com/2-54MM-Female-Double-Connector-Wires/dp/B07XNWD58H?s=hi) | Pack of 20
2-pin JST cables | 22 AWG 2 Pin JST XH2.54 Connector Plug | 2 | $0.50 | $1.00 | Amazon (https://www.amazon.com/mxuteuk-XH2-54-Connector-Female-JST-XH2-54/dp/B083HWDPSV?s=hi) | Pack of 20, 10 usable
Battery | TalentCell Rechargeable 12V Lithium Ion Battery | 1 | $39.99 | $39.99 | Amazon (https://www.amazon.com/TalentCell-Rechargeable-12000mAh-Multi-led-indicator/dp/B00ME3ZH7C)
DC Power Jack | DC Power Jack Plug Adapter | 1 | $1.00 | $1.00 | Amazon (https://www.amazon.com/DAYKIT-Female-2-1x5-5MM-Adapter-Connector/dp/B01J1WZENK) | Pack of 10

### 3.3 Flow Meter

Designator | Component | Qty. | Cost per Unit | Total Cost | Source of Materials | Notes
USFM | TUF-2000M | 1 | $253.00 | $253.00 | Amazon (https://www.amazon.com/VTSYIQI-TUF-2000M-TS-2-Ultrasonic-Waterproof-DN15-100mm/dp/B07JNR2HGW)
Transducer | TS-2 Pair | 1 | (included) | -
Transducer Cable | Transducer Cable | 5 m | (included) | -
Hose Clamps | Hose Clamps | 2 | (included) | -
Heat Shrink | Heat Shrink | 8 | (included) | - | | 2x Red 2x Blue 4x Black small
Spades | Fork Spade U-Type Connectors | 6 | (included) | -
Large black heat shrink | 1/4" 3:1 adhesive lined heat shrink | 5 | $0.05 | $0.25 | Amazon (https://www.amazon.com/gp/product/B0919J58MH/ref=ppx_yo_dt_b_search_asin_title?ie=UTF8&th=1) | 20 ft, each cable needs 2.5"
Solder seal connectors | Marine grade solder seal connectors 18-22 gauge | 6 | $0.20 | $1.20 | Amazon (https://www.amazon.com/Connectors-Haisstronica-Electrical-Waterproof-Automotive/dp/B07C3MKM3K?hvadid=259499196890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) | Pack of 50, 1.5" long
Silicon Lubricant | Dow Corning 111 O-Ring Silicone Lubricant | 1 | $7.95 | $7.95 | Amazon (https://www.amazon.com/Dow-Corning-Molykote-Oring-Lubricant/dp/B075Y5DCY9?s=industrial)

### 4. Build Instructions

### 4.1 FloDar printed circuit board (PCB) assembly

Tools: soldering iron, solder, solder paste, reflow oven or heat gun, hot glue gun and glue, fan for solder fumes (optional), fume hood (optional)

### 4.1.1 ADS1115

Components:

- ADS1115 (with included male headers)

Procedure:
1. Solder provided male headers on to the ADS1115 with the short end of the pins sticking up through the top of the board (Figure 7).

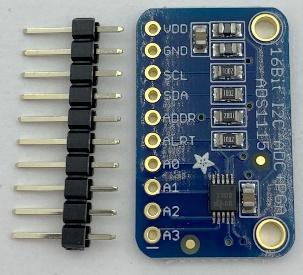
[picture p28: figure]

Figure 7: ADS1115 top with male headers separate (left), and with headers attached (right).

### 4.1.2 Custom PCB

Components (Figure 8):

- Custom PCB
- Female headers (10)
- Male headers (14, 16)
- Resistor
- 3 pin JST XH socket
- 3 pin JST XH plug with wires

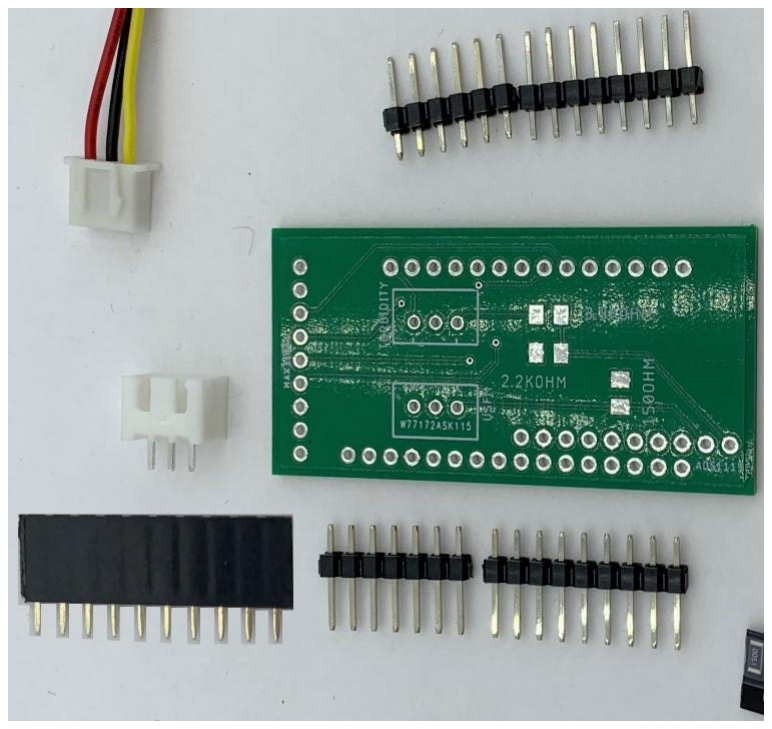
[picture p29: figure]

Figure 8: Components for breakout board assembly.

Procedure:
1. Apply solder paste to pads adjacent to 150 Ohm label (Figure 9, top)
2. Place the resistor across the two pads (direction does not matter).

3. Use either a reflow oven or heat gun (~350°C) to heat the solder paste enough to connect the resistor to the PCB (Figure 10). Paste should go from looking grainy to shiny.
4. Insert the short side of the 14 and 16 long male headers from the bottom of the board into the holes labeled for Hypnos Control in Figure 9, and solder them into place from the top (Figure 10).
5. Insert the pins for the female header into the board from the top side in the holes labeled ADS1115, flip over the board, and solder into place (Figure 10).
6. Insert the pins for the JST socket into the through holes labeled USFM from the top of the board, flip over the board, and solder into place (Figure 10). For consistency, align the side with the cutouts toward the center as indicated by the two lines inside the rectangle for the JST socket on the PCB silkscreen.
7. For the JST plug with cable, plug into the JST socket to determine which wire will be closest to the USFM label. Remove the socket and remove with tweezers or cut flush all wires except the one that will be closest to the USFM label (Figure 10). Plug back into the socket and hot glue wire into place.

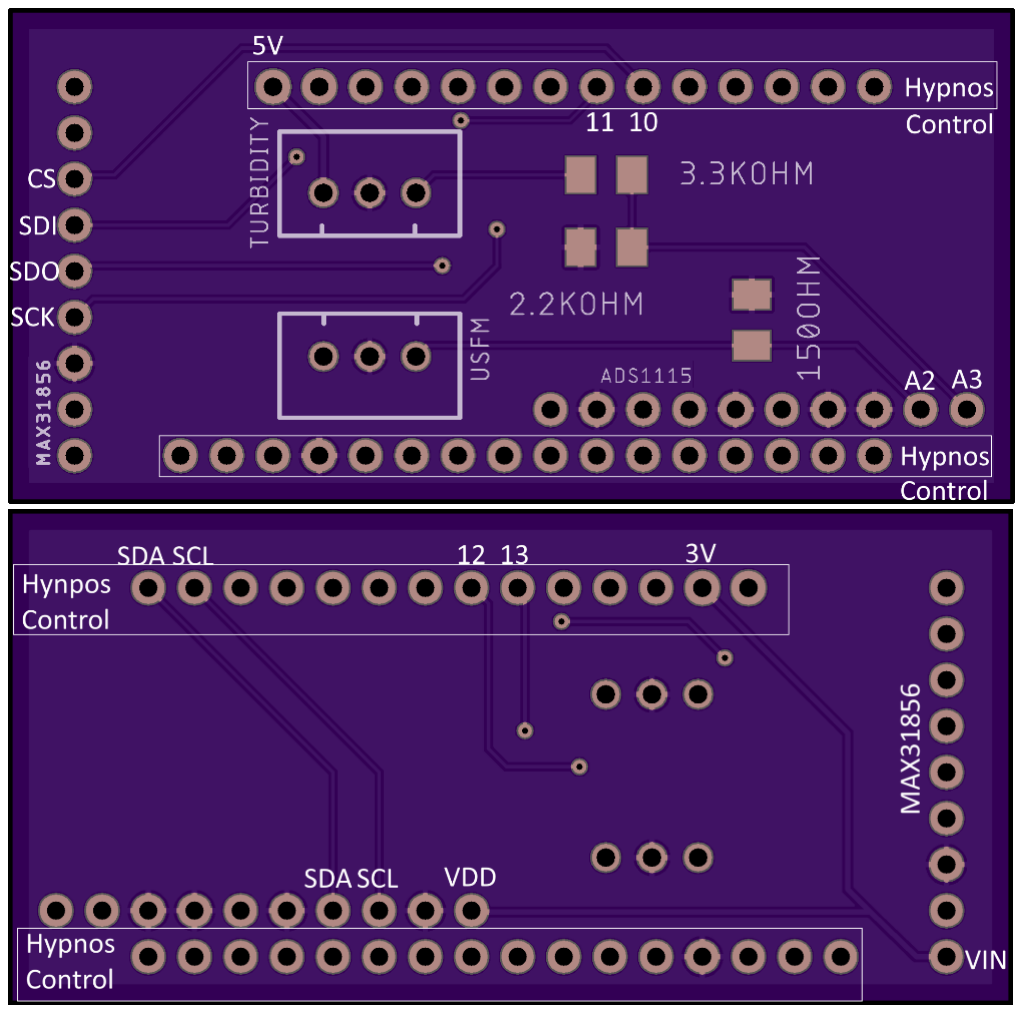
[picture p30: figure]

Figure 9: Custom PCB front (top) and back (bottom) with added labels. Note through holes labeled for MAX31856 are for implementation with a thermocouple. Through holes labeled for turbidity and 3.3 kOhm and 2.2 kOhm resistors are for implementations with a turbidity sensor.
Credit: OSHPark rendering of Gerber file.

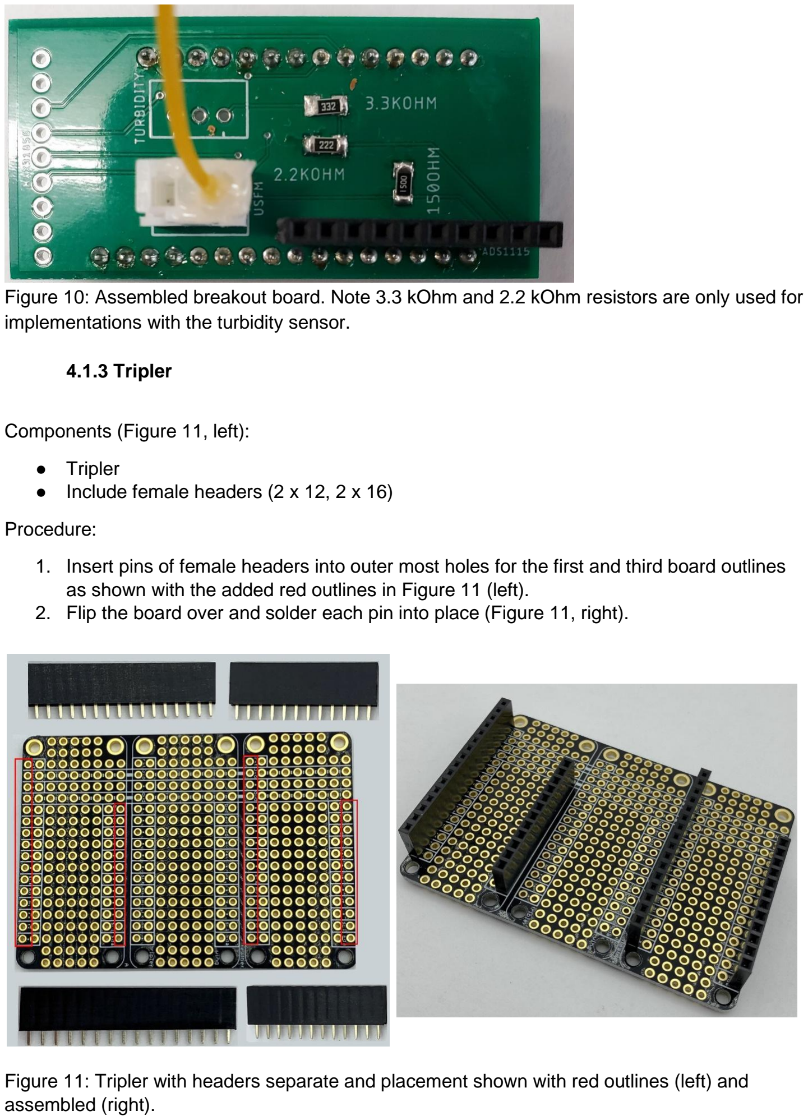
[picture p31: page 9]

Figure 10: Assembled breakout board. Note 3.3 kOhm and 2.2 kOhm resistors are only used for implementations with the turbidity sensor.

### 4.1.3 Tripler

Components (Figure 11, left):

- Tripler
- Include female headers (2 x 12, 2 x 16)

Procedure:

1. Insert pins of female headers into outer most holes for the first and third board outlines as shown with the added red outlines in Figure 11 (left).
2. Flip the board over and solder each pin into place (Figure 11, right).

Figure 11: Tripler with headers separate and placement shown with red outlines (left) and assembled (right).

### 4.1.4 Hypnos

Components (Figure 12):

- Assembled Hypnos PCB (Nguyen et al. 2021)
- Male headers 12, 16
- Female headers 14, 16
- 2 2-pin right angle male JST sockets
- 2 2-pin female JST plugs with wires
- CR1220 coin cell
- microSD card

Procedure:
1. Insert the short side of the male headers from the back side of the board into the through holes labeled Feather starting with the holes closest to the end with the microSD socket (Figure 13, left). Flip over the board and solder each pin into place.

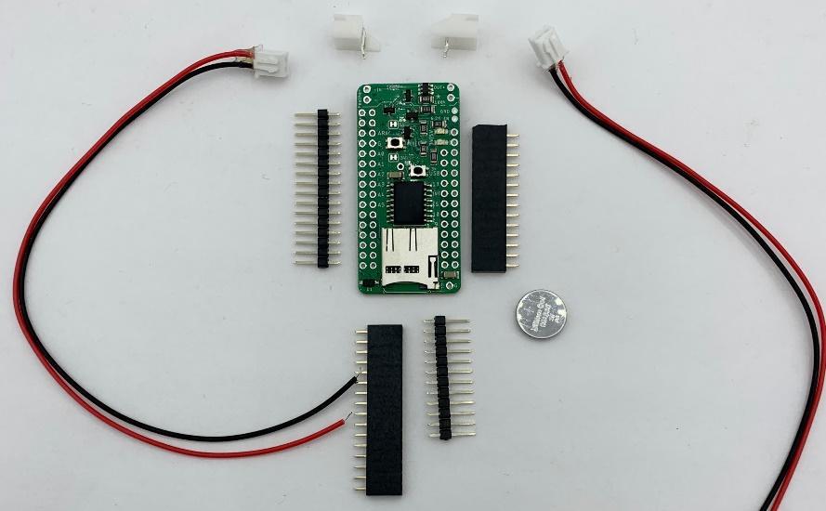
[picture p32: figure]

Figure 12: Top of assembled Hypnos PCB with components to be added. Note 2 pin JST on left has a clipped fin and microSD card is not shown.

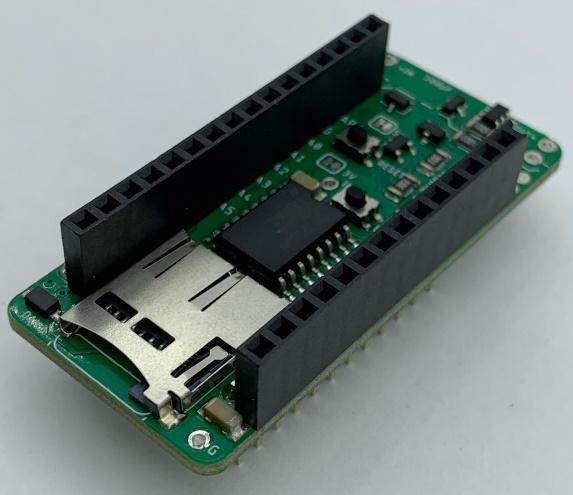
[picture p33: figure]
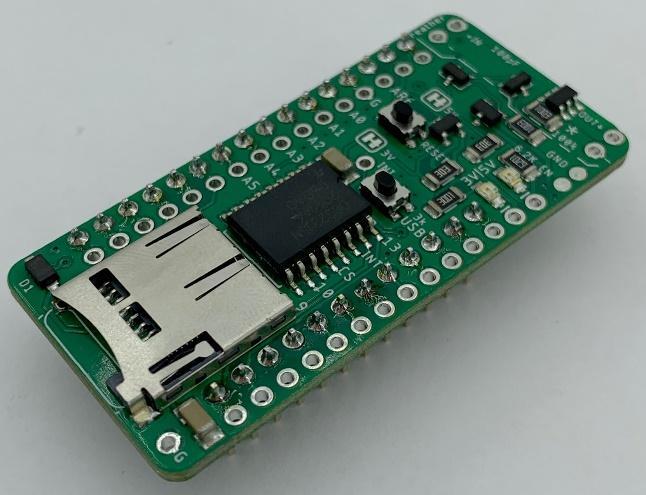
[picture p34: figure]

Figure 13: Top of assembled Hypnos PCB with male headers attached (left), and male and female headers attached (right).

2. Insert the pins of the female headers into the through holes on the PCB labeled control from the top side (Figure 13, right). Flip over the PCB and solder each pin into place.
3. Clip the right fin off of one of the 2 pin right angle JST sockets (Figure 14). Insert from the top into the top of the board in the two through holes labeled “In” so that the entry is facing out from the board. Flip over the board and solder into place.
4. Insert the other 2 pin right angle JST socket from the top into the top of the board in the two through holes labeled “Out” so that the entry is facing out from the board (Figure 14). Flip over the board and solder into place.

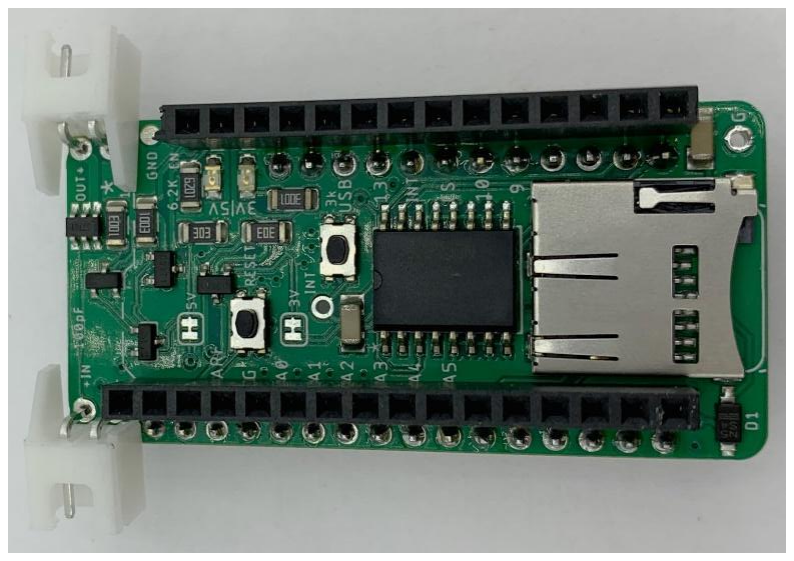
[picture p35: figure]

Figure 14: Top of assembled Hypnos PCB with headers and 2 pin right angle JST sockets.

5. Insert the JST plugs into the sockets. Verify the polarity matches the board for both: red wire at the end where the + symbols is on the board, black wire closer to the headers (Figure 15). If it does not match, use tweezers to gently pull up the plastic tabs holding the crimped connectors inside the case for each wire, pull out the wires, and insert on the appropriate side. Add hot glue to where the wires come out of the case to help hold in place.

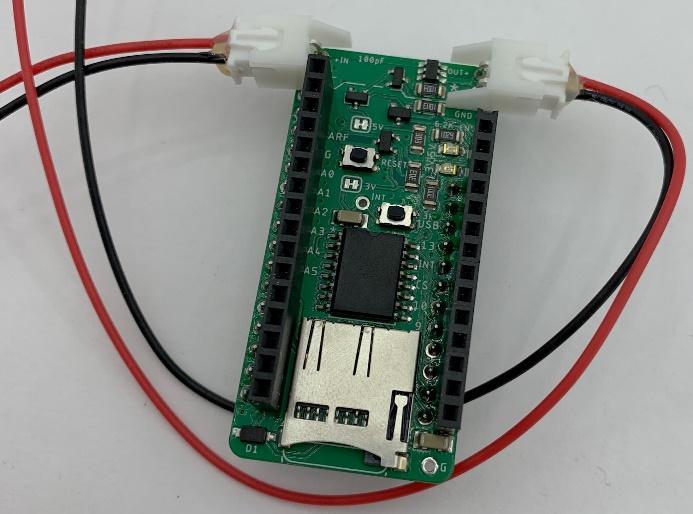
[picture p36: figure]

Figure 15: Fully assembled Hypnos showing correct wire positions.

6. Insert the coin cell into the coin cell holder on the back of the Hypnos board.
7. Insert the microSD card into the microSD socket on the front of the Hypnos board.

### 4.1.5 Feather M0

Components:

- Feather M0
- Included male headers (12, 16)

Procedure:

1) Insert the short end of the male header pins into the Feather M0 board from the bottom (Figure 16, right).
2) Flip the board over, and solder each pin.

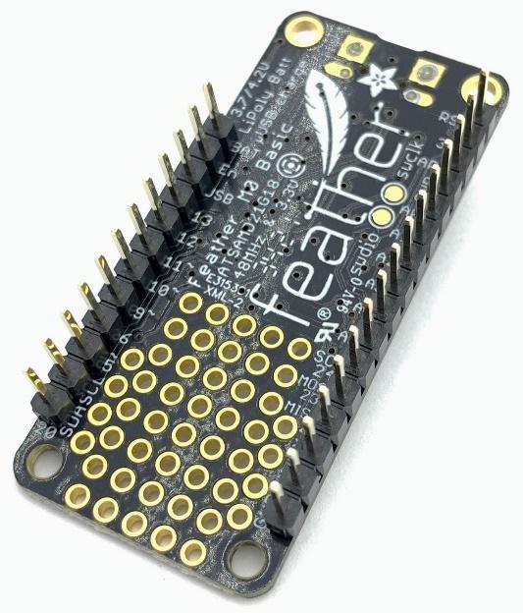
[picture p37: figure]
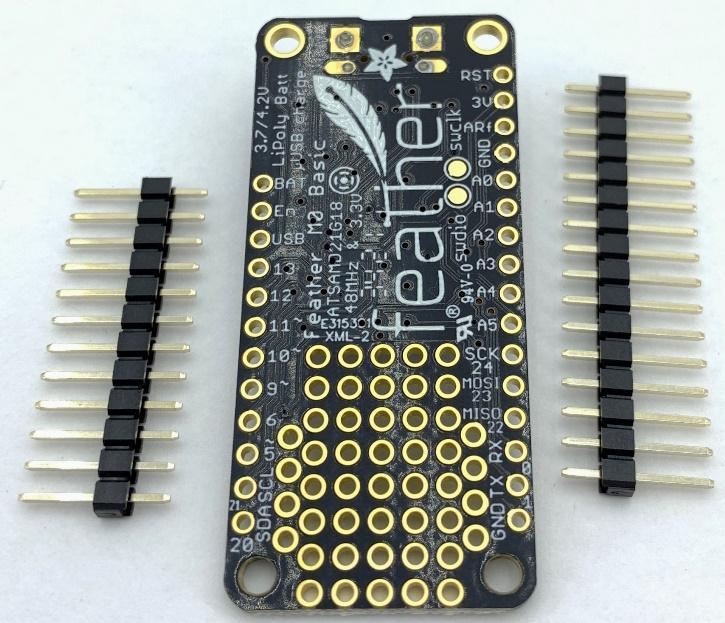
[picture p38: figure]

Figure 16: Feather M0 bottom with separate headers (left) and assembled (right).

### 4.1.6 Conformal coating

In a well-ventilated area or fume hood, coat all surfaces on all PCBs with conformal coating except 1) the unsoldered side of male header pins, 2) on and around buttons, 3) the microSD socket, and 4) the coin cell holder. Leave to dry for up to 48 hours.

### 4.2 FloDar transducer assembly

Tools: Phillips Screwdriver, Flush Cutters, Wire Strippers (22 Gauge, 10 or 12 Gauge), Soldering Iron, Heat Gun (1500 W recommended), Crimpers, Fan for Solder Fumes (Optional)

Components (Figure 17):

- Transducers
- 5 m Transducer Cable
- Electrical Tape
- 2x Large Heat Shrink
- 2x Large Blue and Red Head Shrink
- 2x Waterproof Cable Connectors
- 6x Fork Spade U-Type Connectors
- 6x Solder seal connectors

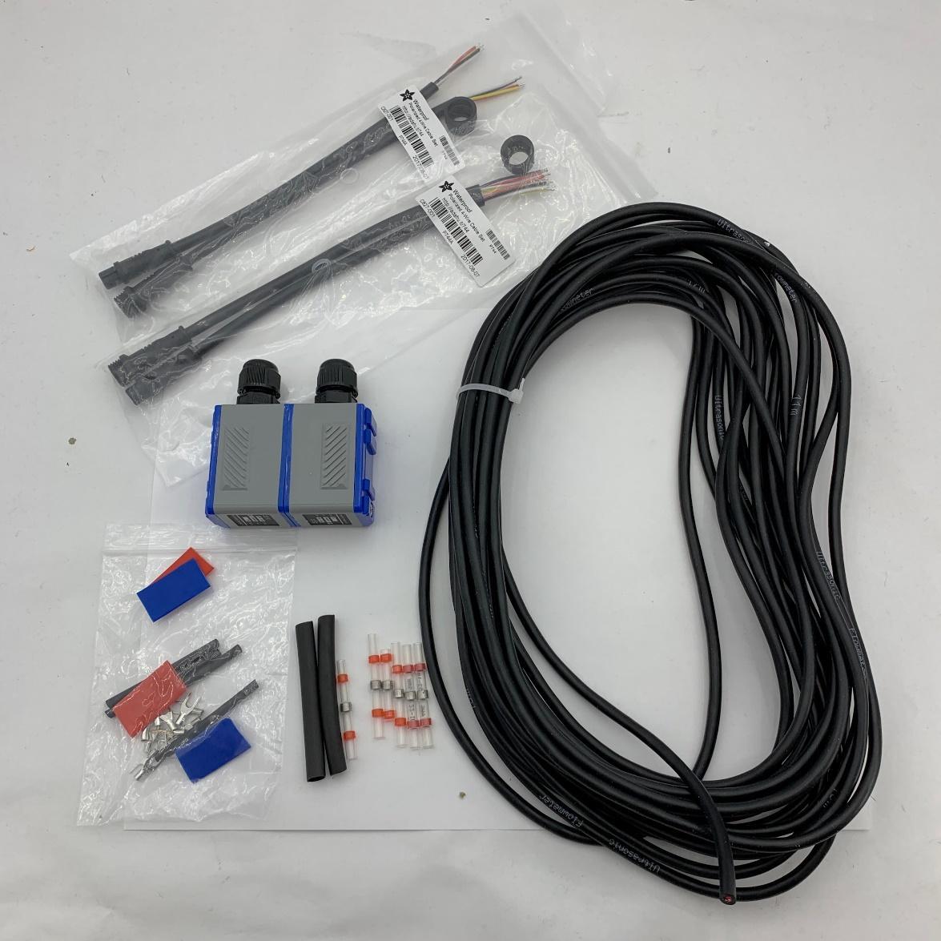
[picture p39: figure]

Figure 17: Materials for assembling transducers

### 4.2.1 Transducer heads

1. Measure and cut each transducer cable in half to have two cables approximately 2.5 m in length (or less depending on location of transducers vs. pelican case).
2. Split all the components into two equal piles.

Repeat steps 3 through 21 for each transducer:

3. Strip back the outer jacket of the transducer cable at one end using the larger gauge strippers, about 3 cm (Figure 18). Note there is a copper wire casing - do not remove this - as well as a thread strand.

Figure 18: Transducer cable with outer jacket stripped back.

4. Unwind the copper, keeping it as intact as possible.
5. Isolate the thread, and cut it out using the flush cutters.
6. Twist the copper tightly to form a cleaner and more usable wire.
7. Strip the black and red cables using the smaller gauge wire strippers for about 0.5 to 1.25 cm (Figure 19).

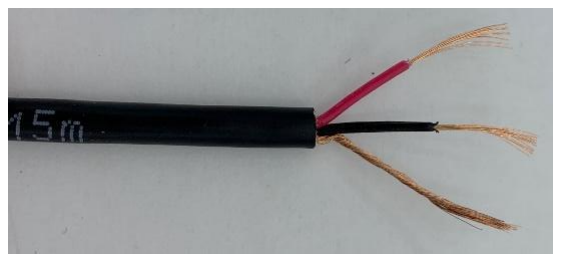
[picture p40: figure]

Figure 19: Transducer cable with outer jacket and individual wire jackets stripped back.

8. Twist the copper in the black and red wires so they are neat as well. Set aside.
9. Unscrew the screw in the lid on the transducer head and remove the lid (Figure 20).

Figure 20: Transducer head with lid removed.

10. Take off the cable gland cap on the transducer head.
11. Poke a hole in the cable gland either using the flush cutters or other sharp object.
12. Use a round blunt object such as your screwdriver to loosen the hole in the cable gland. Be careful not to rip the gland. If the gland comes out of the housing but is undamaged, it is acceptable to place the gland back in its housing.
13. Slide the cable gland cap over the transducer cable such that the side with the threads is facing the stripped end (Figure 21). If you do this step backwards, you are still able to take the cap off the other end of the transducer and flip it around. This will NOT always be the case.

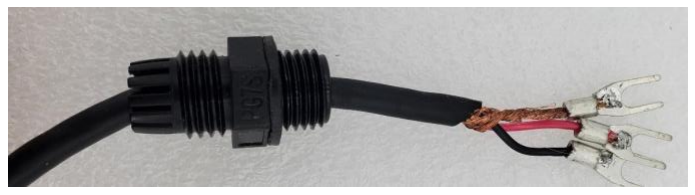
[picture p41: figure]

Figure 21: Transducer wire with cable gland nut (left) and cable gland body (right). Note that the cable gland body right side should still be screwed into the transducer head unlike as shown.

14. Feed the stripped wires into the cable gland body and pull it through such that the stripped wires are on the inside of the transducer and the outermost casing of the transducer wire is through the cable gland (Figure 21). It may help to fold the exposed metal back on itself.
15. Slide a fork spade onto the end of each wire.
16. Optional: Solder each wire end to the fork spade just after the crimp section. Ensure the fan is on prior to soldering.
17. Crimp each fork spade onto each wire. It may help to note the sequence that the wires are placed into the transducer and orient the fork spades so that they are facing up (Figure 20, 22). Ensure that each crimp holds tight.
a. Red goes to the (+)
b. Black goes to the (-)
c. The bare copper goes to the ground .
18. Unscrew each connection without fully taking the screw out. Place the fork spades under the screw and the square washer. It may be necessary to pull or push the transducer cable through the cable gland more to adjust where the fork spades land due to the small space.
19. Screw each of the contacts back down, ensuring that each one is tight and does not move (Figure 22).

Figure 22: Wires with fork spades attached inside transducer head. Note the cable gland nut is not shown but should already be on the cable in orientation shown in Figure 21 (top).

20. To seal the container, apply RTV silicone to the top of the outer edge of the grey body part where it will interact with the blue lid. Ensure that the top side of inside nut of the cable gland is horizontal so it does not interfere with the lid.
21. Place the transducer top back on the transducer and screw it back down. Be careful not to screw back in at an angle as you are screwing directly into the plastic. Also ensure that the top forms a tight seal against the transducer body, cracks could allow water to seep into the transducer and cause shortage.
22. Screw the cable gland cap that was already on the transducer cable tightly onto the cable gland to grip the transducer cable.
23. If this is the first transducer, repeat for the second transducer.

### 4.2.2 Transducer cable to waterproof connector cable

Repeat steps 1 to 10 for each transducer:

1. Slide a 6 cm long piece of the large black heat shrink over the untouched end of the transducer cable.
2. Strip the outer jacket of the transducer cable back about 4.5 cm: enough to fit a solder seal connector with 1.5 cm of wire exposed (similar to Figure 18).
3. Same as before, unwind the copper casing and isolate the thread, cutting it off. Twist the copper neatly together.
4. Strip back the jackets of the red and black wires using the smaller strippers about 1.5 cm (similar to Figure 19). Twist the copper strands for each wire together.
5. Slide the large black heat shrink at least 10 cm away from the end of the transducer cable.
6. Switching to the waterproof connector cable, identify whether this is the up (red) or down (blue) transducer, and place the respective color heat shrink on the wire end of the each side of the connector cable and slide to next to the threads or connector. Use a heat gun to shrink on to each cable (Figure 23). This is a critical step; if forgotten, you may not be able to place the heat shrink on after further steps are completed.
7. For remaining steps, use the side of the connector cable that has threads for the transducers. Set aside the side that the cap goes over. It is used for the pelican case.

Figure 23: Waterproof connector cable with blue heat shrink to indicate down transducer, and heat shrinked connections to transducer cable (completed in step 10).
8. Strip the jackets about 1.5 cm of all four wires on the connector cable using the smaller gauge wire strippers (Figure 24).

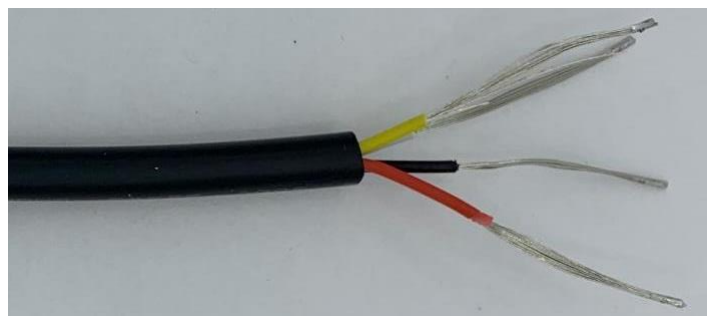
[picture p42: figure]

Figure 24: Waterproof connector cable with wire jackets stripped.

9. For each of the three transducer wires:
a. Slide on a solder seal connector.
b. Twist the wire from the waterproof connector cable around the appropriate transducer cable wire:
Waterproof connector cable wire color | Transducer cable wire color
Red | Red
Black | Black
White, Yellow | Bare
c. Slide the solder seal connectors so that the metal ring of solder is on top of each of the combined wires (Figure 25).
d. Make sure the fan is on, if using, and use a heat gun at ~200°C or the highest setting for a 1500 W heat gun to first melt the solder and then shrink the surrounding tube one side at a time.

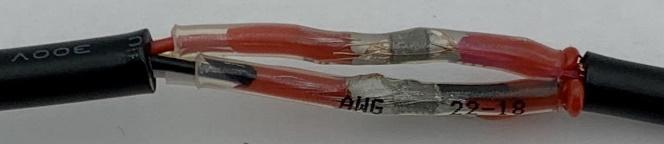
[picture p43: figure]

Figure 25: Waterproof connector cable and transducer cable wires with solder seal connectors prior to heating (left) and after heating (right). Note directions indicate putting on and heating each connector individually, not all together as shown on the left.

10. Slide the large black heat shrink over all three wire connections, and use the heat gun to shrink the heat shrink (Figure 23).
11. If this is the first transducer, repeat for the second transducer.

### 4.3 Pelican case assembly

### 4.3.1 Cable glands

Tools: drill or drill press, drill bit

Components:

- Pelican case
- 2x cable glands
- Marine epoxy

Procedure:

1. Take out the bottom foam piece in the case, and discard.
2. Use the drill and drill bit to drill two 1.25 cm diameter holes in the right side (when looking at the pressure valve) of the pelican case at 4.5 cm from the bottom and 4.4 cm from each side (Figure 26). Hole locations do not need to be exact, but ensure that the cable gland nuts will sit on top of the vertical ridges inside, and centers will be above the flowmeter to allow for each cable to pass above the flowmeter. Alternatively, the holes could be drilled in the front of the box to align with the connections for the flowmeter.

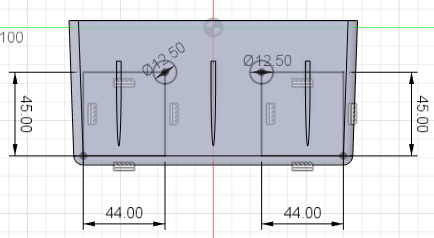
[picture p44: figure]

Figure 26: CAD rendering of the side of the pelican case showing hole placements with measurements in mm.

3. Unscrew the flat nuts. The rubber gaskets can be used if the nut is put on backward inside the box or the rubber gasket can be removed and epoxy used to seal the gland instead.
4. Mix the two parts of the epoxy, and apply to the base of the threads of each cable gland on the side for the flat nut. Insert cable glands into the holes in the pelican case from the outside, and fasten on the inside with the flat nut (Figure 27).

Figure 27: Cable gland in pelican case shown from outside (left) and inside (right).

### 4.3.2 Insert

Tools: 3D printer or laser cutter

Components:

- acrylic or ASA filament

Procedure:

1. 3D print or laser cut the insert. If using the acrylic insert, after cutting, glue the four flow meter tabs into place with Acrylic Plastic Cement (e.g. Weld-On 3).
2. Insert the 2-4 bolts for the tripler into the 3 mm holes in the insert from the bottom (see orientation in Figure 3) and fasten in place with nuts.
3. Put the insert into the case with the flow meter section on the right and the bolt threads up (Figure 2, 3).

### 4.3.3 Final Assembly and Wiring

Tools: Small screwdriver, scissors

Components:

- Pelican case with insert
- PCBs: ADS1115, custom breakout board, Hypnos, Feather M0, tripler
- Unattached waterproof connector cables
- USB cord
- DC power jack
- Flow meter
- Battery (fully charged)
- Velcro

Procedure:

1. PCBs
a. Set the tripler on the bolts in the insert, and use one nut on each to fasten in place.
b. Stack the Hypnos board on the headers on the left side of the tripler (Figure 28).
c. Stack the custom breakout board on top of the Hypnos board (Figure 28).
d. Stack the ADS1115 board on top of the custom breakout board (Figure 28).

e. Stack the Feather M0 on the headers on the right side of the tripler (Figure 28).
f. If the male and female headers are switched (male for control and female for Feather) on the Hypnos, the Hypnos will need to be stacked under the M0 instead of the custom PCB.
g. Connect the USB cable to the USB port on the Feather M0.

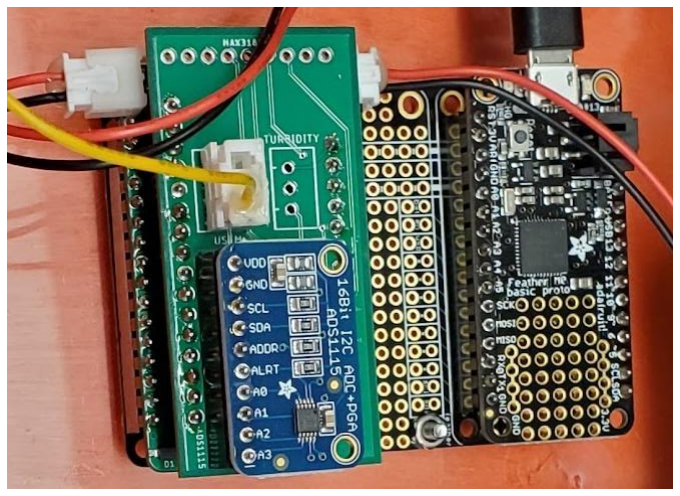
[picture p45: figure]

Figure 28: PCBs stacked with connections.

2. Battery
a. Put the battery upright in the case in the long slot against the back so that there is room to make connections (Figure 2, 3).
b. Connect the other end of the USB cable to the battery. Make sure any excess cable length will not get closed in the case seams.
c. Unscrew the terminals on the DC power jack, insert the ends of the wires (red to + and black to -) from the JST connector in the “In” location on the Hypnos, and screw back down.
d. Insert the DC power jack into the battery barrel jack socket.
3. Flow meter
a. Cut a ~25 cm long piece of velcro, and slide it under the insert. For the 3D printed insert, the velcro comes up in the oval holes above and below the flow meter. For the laser cut insert, the velcro comes up in the battery slot and the narrow space between the insert and case wall (Figure 2).
b. On the flow meter, unscrew the terminals for 24+, 24-, A0, UP+, UP-, GND, DN+, DN-, and GND (Figure 29).
c. For each of the waterproof connector cables, slide the nut onto the unthreaded side with the threads facing away from the bare wires (Figure 30).
d. Loosen the nuts on the outside of the cable glands in the pelican case.
e. Insert, bare wires first, the waterproof connector cable with the red heat shrink for the upstream transducer in the cable gland closer to the handle (Figure 30).
f. Insert, bare wires first, the waterproof connector cable with the blue heat shrink for the downstream transducer in the cable gland closer to the hinge (Figure 30).
g. For the upstream cable, insert the end of the red wire into UP+ terminal, and tighten down the screw. Insert the end of the black wire into the UP- terminal, and tighten down the screw. Insert the ends of the white and yellow wires into the

GND terminal between the UP- and DN+ terminals, and tighten down the screw (Figure 29).
h. For the downstream cable, insert the end of the red wire into DN+ terminal, and tighten down the screw. Insert the end of the black wire into the DN- terminal, and tighten down the screw. Insert the ends of the white and yellow wires into the farthest right GND terminal, and tighten down the screw (Figure 29).
i. Insert the end of the red wire from the “Out” JST of the Hypnos into the 24+ terminal, and tighten down the screw.
j. Insert the end of the black wire from the “Out” JST of the Hypnos into the 24-terminal, and tighten down the screw.
k. Insert the end of the wire from the 3 pin JST on the custom breakout board into the A0 terminal, and tighten down the screw.
l. Rotate the flow meter and set into place, and secure with the velcro (Figure 2).
m. Tighten the outer nuts on the cable glands.

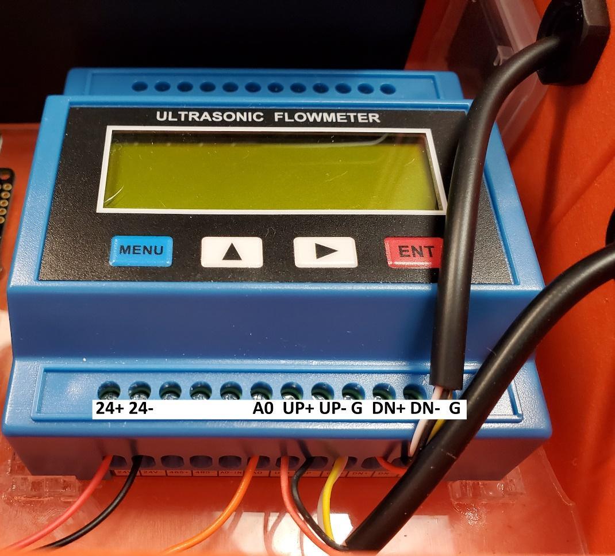
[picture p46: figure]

Figure 29: Flow meter with all wire connections. Note labels are below the ports for the wires, so in the image labels have been duplicated next to the screw terminals for clarity.

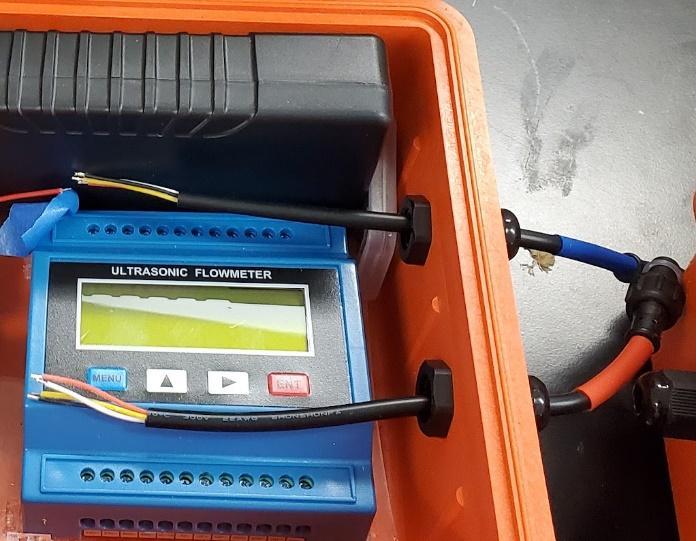
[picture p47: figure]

Figure 30: Pelican case with waterproof connector cables, battery, and flow meter.

### 4.4 Program Feather M0

1. Follow the directions on the Loom Wiki for installation of the Arduino IDE and Loom 4.1 Board profile: https://github.com/OPEnSLab-OSU/Loom-V4#Install
2. Download the FloDar_Field_Loom4_1.ino, (https://github.com/OPEnSLab-OSU/FloDar/blob/main/Software/Loom%204/FloDar_Field_Loom4_1/FloDar_Field_Loom4_1.ino) and place in a folder with the same name (FloDar_Field_Loom4_1).
3. Open the .ino file with the Arduino IDE.
4. Adjust constants as desired:
a. Time period between measurements: DAY, MINUTE, HOUR, SECOND on lines 21-24
b. Maximum flow rate: MAXFLOWRATE on line 31 (Must match flow rate for 20 mA set in flow meter menu 57 in Section 4.5.2).
c. Time zone: Line 36, third variable for Hypnos object creation. See
Loom_Hypnos.h (https://github.com/OPEnSLab-OSU/Loom-V4/blob/main/src/Hardware/Loom_Hypnos/Loom_Hypnos.h) lines 31-53 for options.
5. Follow the directions for selecting a board profile, port and compiling code on the Loom Wiki under “Run an example”, (https://github.com/OPEnSLab-OSU/Loom-V4#run-an-example) but use the FloDar code instead of an example. See also guidance from Adafruit. (https://learn.adafruit.com/adafruit-feather-m0-basic-proto/using-with-arduino-ide)
6. Once the code has successfully compiled, open the serial monitor: Tools\Serial monitor or magnifying glass like icon in upper right corner.
7. Follow the prompts in the serial monitor to set the clock.

### 4.5 Flow meter setup

For the correct speed of sound, and output from the flow meter, many settings need to be changed from the default (see Ultrasonic Flow Meter User Manual for more information). During normal operations, the flow meter is turned on for just long enough to capture a reading. In order to keep the flow meter on for long enough to change parameters, either reprogram the Feather M0 with software to keep the whole system on (e.g. FloDar_Lab.ino (https://github.com/OPEnSLab-OSU/FloDar/blob/main/Software/Loom%204/FloDar_Lab/FloDar_Lab.ino) which includes data logging), or directly wire the 24+ and 24- to the DC power plug for the battery. Turn on the battery. Remember to change the program or wiring after setup is complete.

There are four buttons for navigating and changing parameters on the flow meter:

1) MENU: Allows input of a specific menu number
2) : Increments to greater menu item, or with menu button pressed or changing a parameter cycles through 0-9, +, -, .
3) : Decrements to a lesser menu item or moves the cursor over
4) ENT: Finishes menu number input or enters into a sub menu

### 4.5.1 Speed of sound related parameters

Optional: Menu 30: Set unit system to English (all values below will be in English units)

1. Menu 11: Outer diameter of pipe: 1.906 in
2. Menu 12: Pipe wall thickness: 0.145 in
3. Menu 14: Pipe material: (5) PVC
4. Menu 16: Lining parameters: (0) none, no liner
5. Menu 20: Liquid type: (0) water(general)
6. Menu 23: Transducer type: clamp-on Ts-2
7. Menu 24: Transducer mounting type: (0) V
8. Menu 25: Transducer installation distance: Set by flow meter - verify it is 1.01 in

### 4.5.2 Output and display related parameters

1. Menu 31: Flow rate unit: L/min (or other desired unit that is consistent across the flow meter and Arduino code parameters)
2. Menu 55: Analog output mode: 0-20 mA
3. Menu 56: Value corresponding to 0 mA current: 0
4. Menu 57: Value corresponding to to 20 mA current: 150 (or value that is consistent across the flow meter and Arduino code parameters)

### 4.5.3 Save parameters

Press enter twice in Menu 26 to “solidify settings”: save to internal flash memory. Without this step, none of the parameter changes will remain after power is removed.

### 5. Operation Instructions

### 5.1 Transducer installation

The transducers should be installed on a clean section of pipe that is free of debris or scaling on the outside and inside where there will be steady, full pipe flow with minimal bubbles and suspended sediment. See the Ultrasonic Flow Meter User Manual for more information on transducer placement in a pipe system. Apply lubricant to the oval transducer faces, set the upstream transducer face against the cleaned pipe location with the label on the downstream side, and use the clamp to fasten securely with the clamp band in the gap between raised sections on the back of the transducer (Figure 4). Place the spacer against the upstream transducer and slot the downstream transducer into the spacer, label touching the spacer, or measure and place the downstream transducer at the distance indicated by Menu 25 exactly in line with the upstream transducer, and use the clamp to fasten securely (Figure 4). The spacer can be removed or left in place. Attach the upstream waterproof connector cable from the transducer to the upstream cable attached to the flow meter, and the downstream waterproof connector cable from the transducer to the downstream cable attached to the flow meter.

### 5.2 Flow meter calibration

For the flow meter to accurately calculate fluid velocity, it must have a zero flow reference. Fill the pipe the transducers are attached to with water, and wait until there are no bubbles or fluid movement. Turn on the flow meter and select menu 42 (see Section 4.5). Select ENT to start the zero flow calibration. When calibration is complete, solidify settings in flash memory using menu 26 (see Section 4.5.3).

### 5.3 Deployment

After the transducers are installed, place the pelican case in an adjacent location and open it. Switch on the battery, and wait up to 30 seconds for the flow meter to turn on: initial setup waits for a serial monitor connection for 20 seconds, then the flow meter takes up to 10 seconds to boot up. If the flow meter does not power on, check all wire connections and battery voltage. When the flow meter powers on, check that the flow meter display shows signal quality values greater than 60 for each transducer, and then a flow value within the expected range, and “R” (normal) for the system error code in the upper right corner of the display. If not, consult the Ultrasonic Flow Meter User Manual for troubleshooting. Close and latch the pelican case, ensuring that there are no debris or wires between the gasket in the lid and the bottom lip.

### 6. References

Nguyen, B., Goto, B., Selker, J.S., Udell, C. 2021. Hypnos board: (https://www.sciencedirect.com/science/article/pii/S2468067221000420) A low-cost all-in-one solution for environment sensor power management, data storage, and task scheduling. (https://www.sciencedirect.com/science/article/pii/S2468067221000420) HardwareX, 10: e00213. https://doi.org/10.1016/j.ohx.2021.e00213

Ultrasonic Flow Meter User Manual. Type: TUF-2000M. Accessed from https://m.media-amazon.com/images/I/A12ZQnE3uEL.pdf. Accessed 2023-03-22.

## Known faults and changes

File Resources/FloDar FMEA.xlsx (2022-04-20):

Component Name | Function | Failure Mode | Failure Effect | Failure Cause | Severity | Occurance | Detection | RPN
Transducers | Sense Flowrate
 | Transport Raw Signal
TUF-2000M | Transducer Signal Processing
 | Output Analog Flowrate Signal
Hypnos | Keep RTC
 | Log Data to SD
Feather | Run Control Script
 | Communication between ADS1115
Custom Board | Breakout Boards
 | Divide Analog Voltage
ADS1115 | Convert Analog Signal to I2C
Power Connections | Provide Power to Hypnos
 | Provide Power to TUF-2000M
Signal Connections | TUF-2000M to Board Stack
 | Transducers to TUF-2000M
Waterproof Connectors | Connection between Pelican Case and Transducers
Cable Glands | Watertight Cable Port in Pelican Case
Battery | Power for Entire System
 | Recharge When Not in Use
Pelican Case | Environmental Protection
 | Access to Internals

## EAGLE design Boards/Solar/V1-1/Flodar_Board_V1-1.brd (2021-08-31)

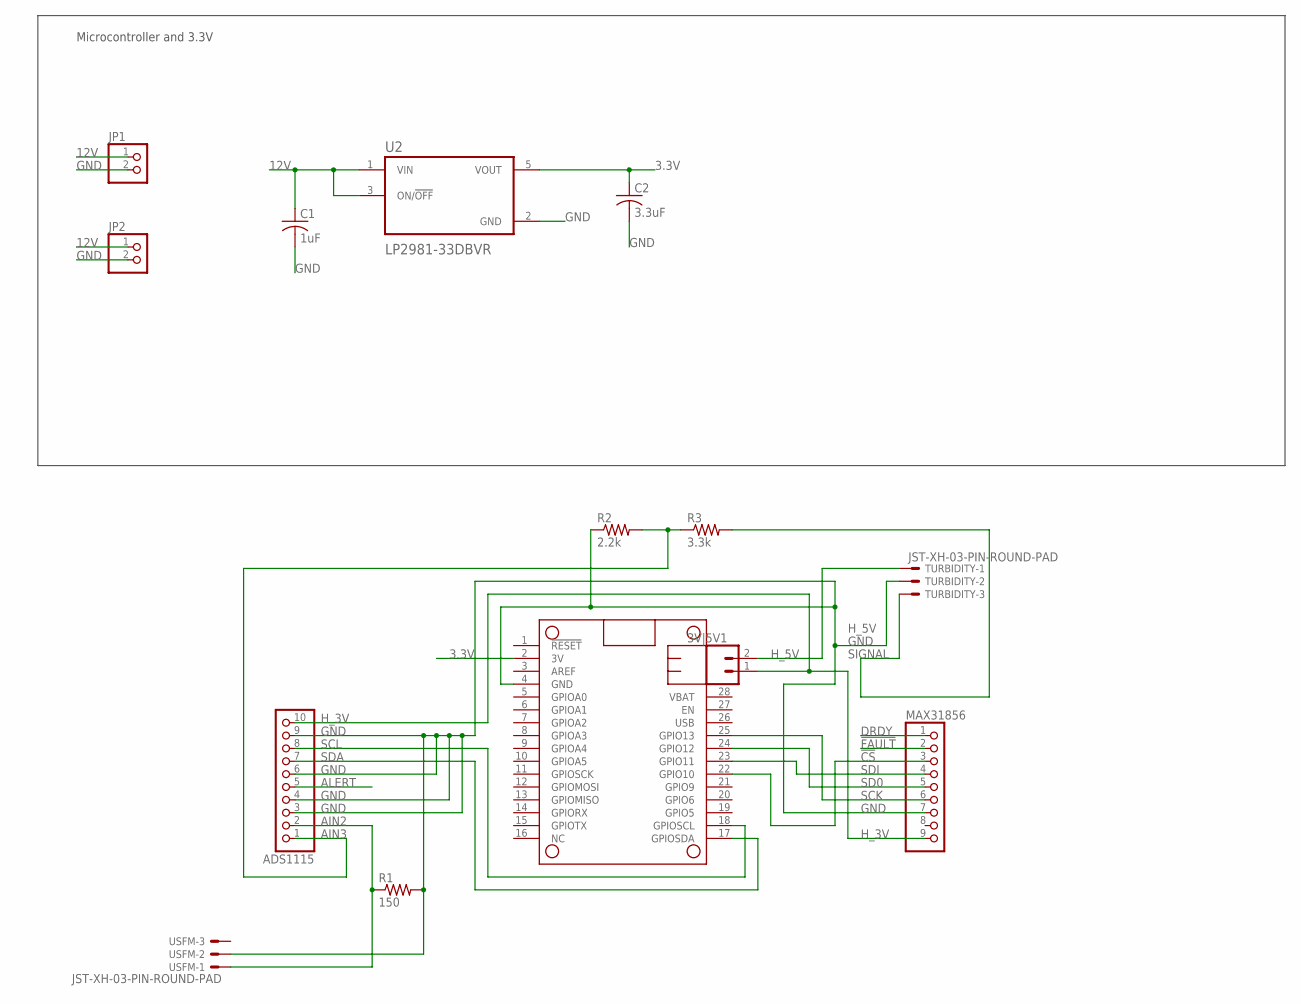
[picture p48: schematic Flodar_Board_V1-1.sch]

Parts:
3V|5V1: CONN_021X02_NO_SILK; 1X02_NO_SILK
ADS1115: HEADER-1X1070MIL; 1X10_ROUND70
C1: 1uF; C1206
C2: 3.3uF; C1206
JP1, JP2: PINHD-1X2; 1X02
MAX31856: HEADER-1X970MIL; 1X09_ROUND_70
MS3: FEATHERWING
R1: 150; R1206
R2: 2.2k; R1206
R3: 3.3k; R1206
TURBIDITY: JST-XH-03-PIN-ROUND-PAD; JST-XH-03-PACKAGE-ROUND-PAD
U2: LP2981-33DBVR; SOT95P280X145-5N
USFM: JST-XH-03-PIN-ROUND-PAD; JST-XH-03-PACKAGE-ROUND-PAD

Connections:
3.3V: C2.1, MS3.2 (3V), U2.5 (VOUT)
12V: C1.1, JP1.1, JP2.1, U2.1 (VIN), U2.3 (ON/!OFF)
!CS: MAX31856.3, MS3.22 (GPIO10)
!FAULT: MAX31856.2
AIN2: ADS1115.2, R1.1, USFM.1
AIN3: ADS1115.1, R2.2, R3.1
ALERT: ADS1115.5
DRDY: MAX31856.1
GND: ADS1115.3, ADS1115.4, ADS1115.6, ADS1115.9, C1.2, C2.2, JP1.2, JP2.2, MAX31856.7, MS3.4 (GND), R1.2, R2.1, TURBIDITY.2, U2.2 (GND), USFM.2
H_3V: 3V|5V1.1, ADS1115.10, MAX31856.9
H_5V: 3V|5V1.2, TURBIDITY.1
SCK: MAX31856.6, MS3.25 (GPIO13)
SCL: ADS1115.8, MS3.18 (GPIOSCL)
SD0: MAX31856.5, MS3.24 (GPIO12)
SDA: ADS1115.7, MS3.17 (GPIOSDA)
SDI: MAX31856.4, MS3.23 (GPIO11)
SIGNAL: R3.2, TURBIDITY.3

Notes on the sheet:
Microcontroller and 3.3V

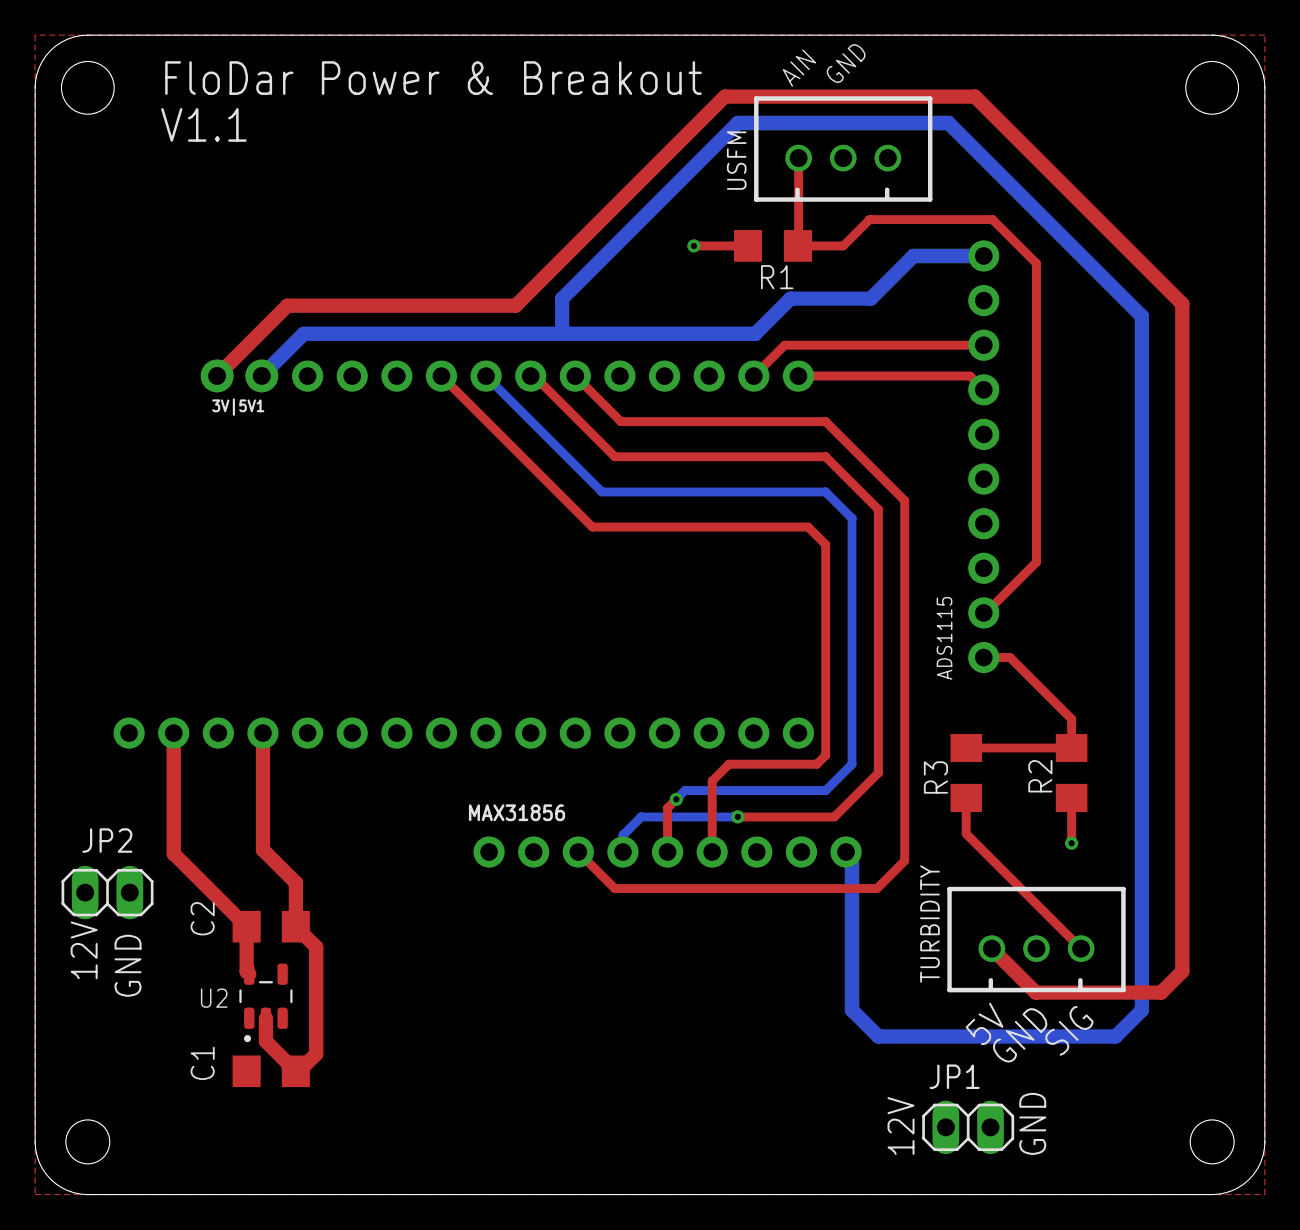
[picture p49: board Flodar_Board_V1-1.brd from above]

Board: 2 copper layers, 70.0 x 66.0 mm, 14 parts (0 on the bottom side), 14 nets.

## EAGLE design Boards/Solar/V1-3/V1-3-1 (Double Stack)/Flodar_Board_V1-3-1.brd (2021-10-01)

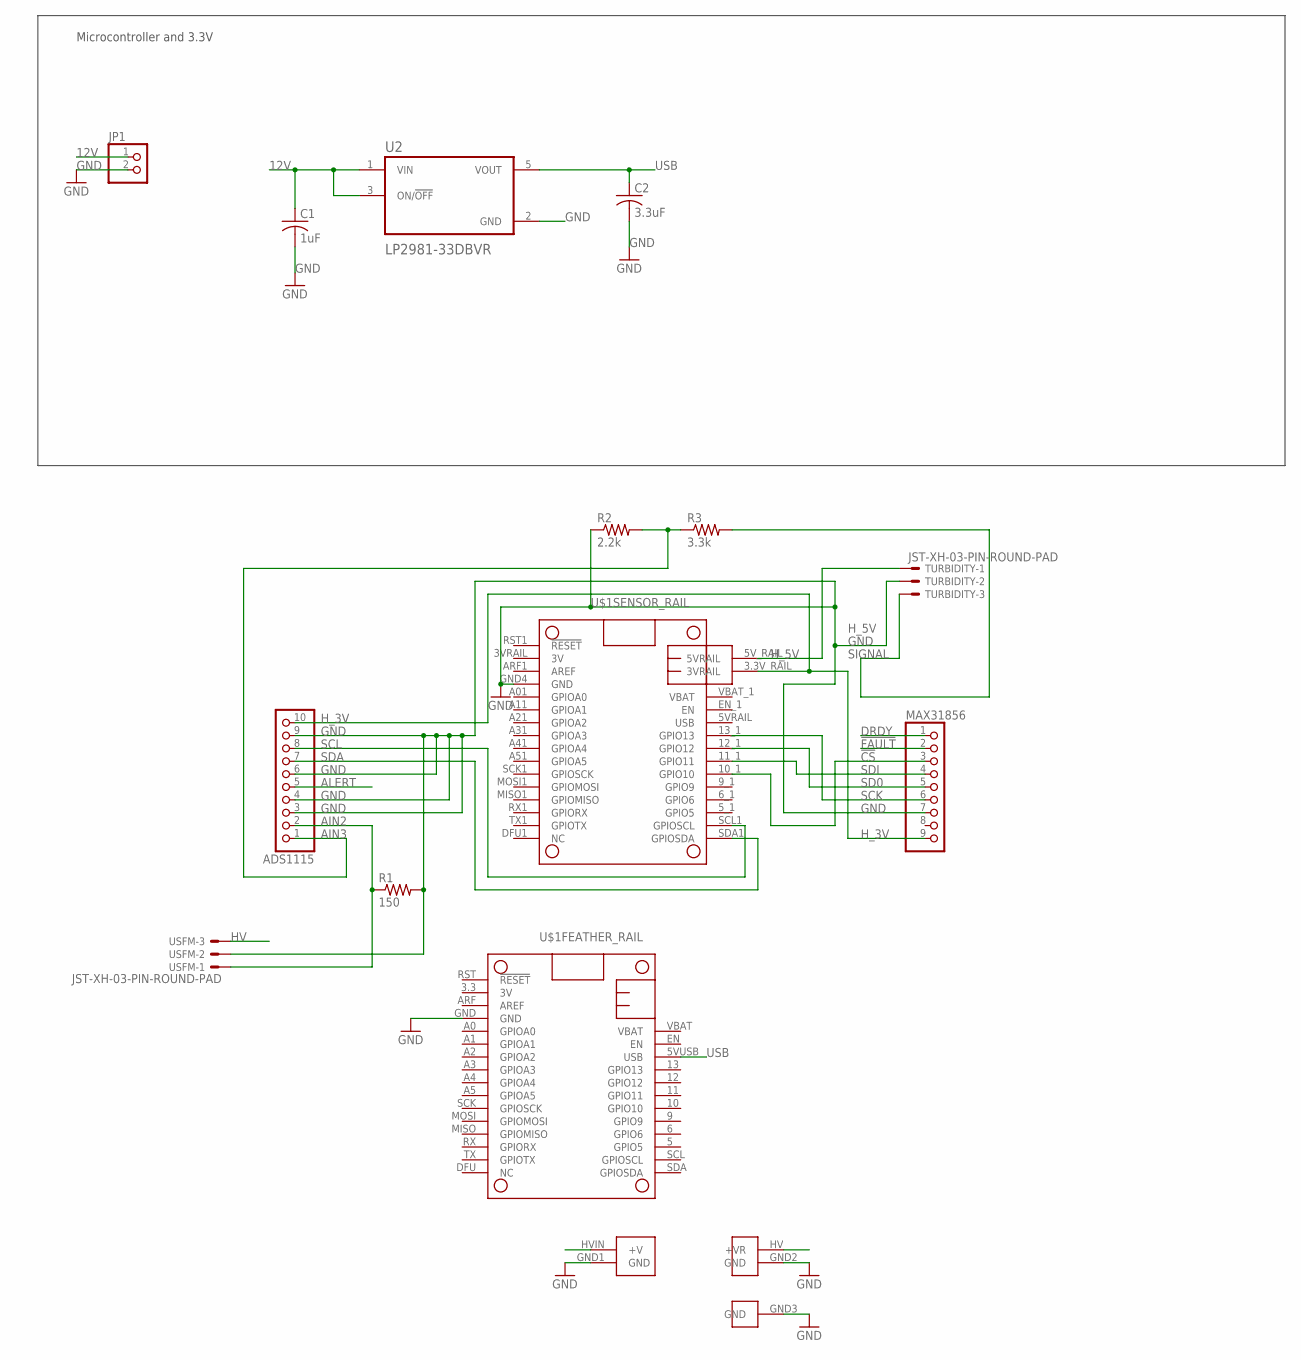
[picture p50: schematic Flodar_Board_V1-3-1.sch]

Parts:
ADS1115: HEADER-1X1070MIL; 1X10_ROUND70
C1: 1uF; C1206
C2: 3.3uF; C1206
JP1: PINHD-1X2; 1X02
MAX31856: HEADER-1X970MIL; 1X09_ROUND_70
R1: 150; R1206
R2: 2.2k; R1206
R3: 3.3k; R1206
TURBIDITY: JST-XH-03-PIN-ROUND-PAD; JST-XH-03-PACKAGE-ROUND-PAD
U2: LP2981-33DBVR; SOT95P280X145-5N
U$1: HYPNOS_V3
USFM: JST-XH-03-PIN-ROUND-PAD; JST-XH-03-PACKAGE-ROUND-PAD

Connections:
12V: C1.1, JP1.1, U2.1 (VIN), U2.3 (ON/!OFF), U$1.HVIN (+V)
!CS: MAX31856.3, U$1.10_1 (GPIO10)
!FAULT: MAX31856.2
AIN2: ADS1115.2, R1.1, USFM.1
AIN3: ADS1115.1, R2.2, R3.1
ALERT: ADS1115.5
DRDY: MAX31856.1
GND: ADS1115.3, ADS1115.4, ADS1115.6, ADS1115.9, C1.2, C2.2, JP1.2, MAX31856.7, R1.2, R2.1, TURBIDITY.2, U2.2 (GND), U$1.GND, U$1.GND1 (GND), U$1.GND2 (GND), U$1.GND3 (GND), U$1.GND4 (GND), USFM.2
HV: U$1.HV (+VR), USFM.3
H_3V: ADS1115.10, MAX31856.9, U$1.3.3V_RAIL (3VRAIL)
H_5V: TURBIDITY.1, U$1.5V_RAIL (5VRAIL)
SCK: MAX31856.6, U$1.13_1 (GPIO13)
SCL: ADS1115.8, U$1.SCL1 (GPIOSCL)
SD0: MAX31856.5, U$1.12_1 (GPIO12)
SDA: ADS1115.7, U$1.SDA1 (GPIOSDA)
SDI: MAX31856.4, U$1.11_1 (GPIO11)
SIGNAL: R3.2, TURBIDITY.3
USB: C2.1, U2.5 (VOUT), U$1.5VUSB (USB)

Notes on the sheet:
Microcontroller and 3.3V

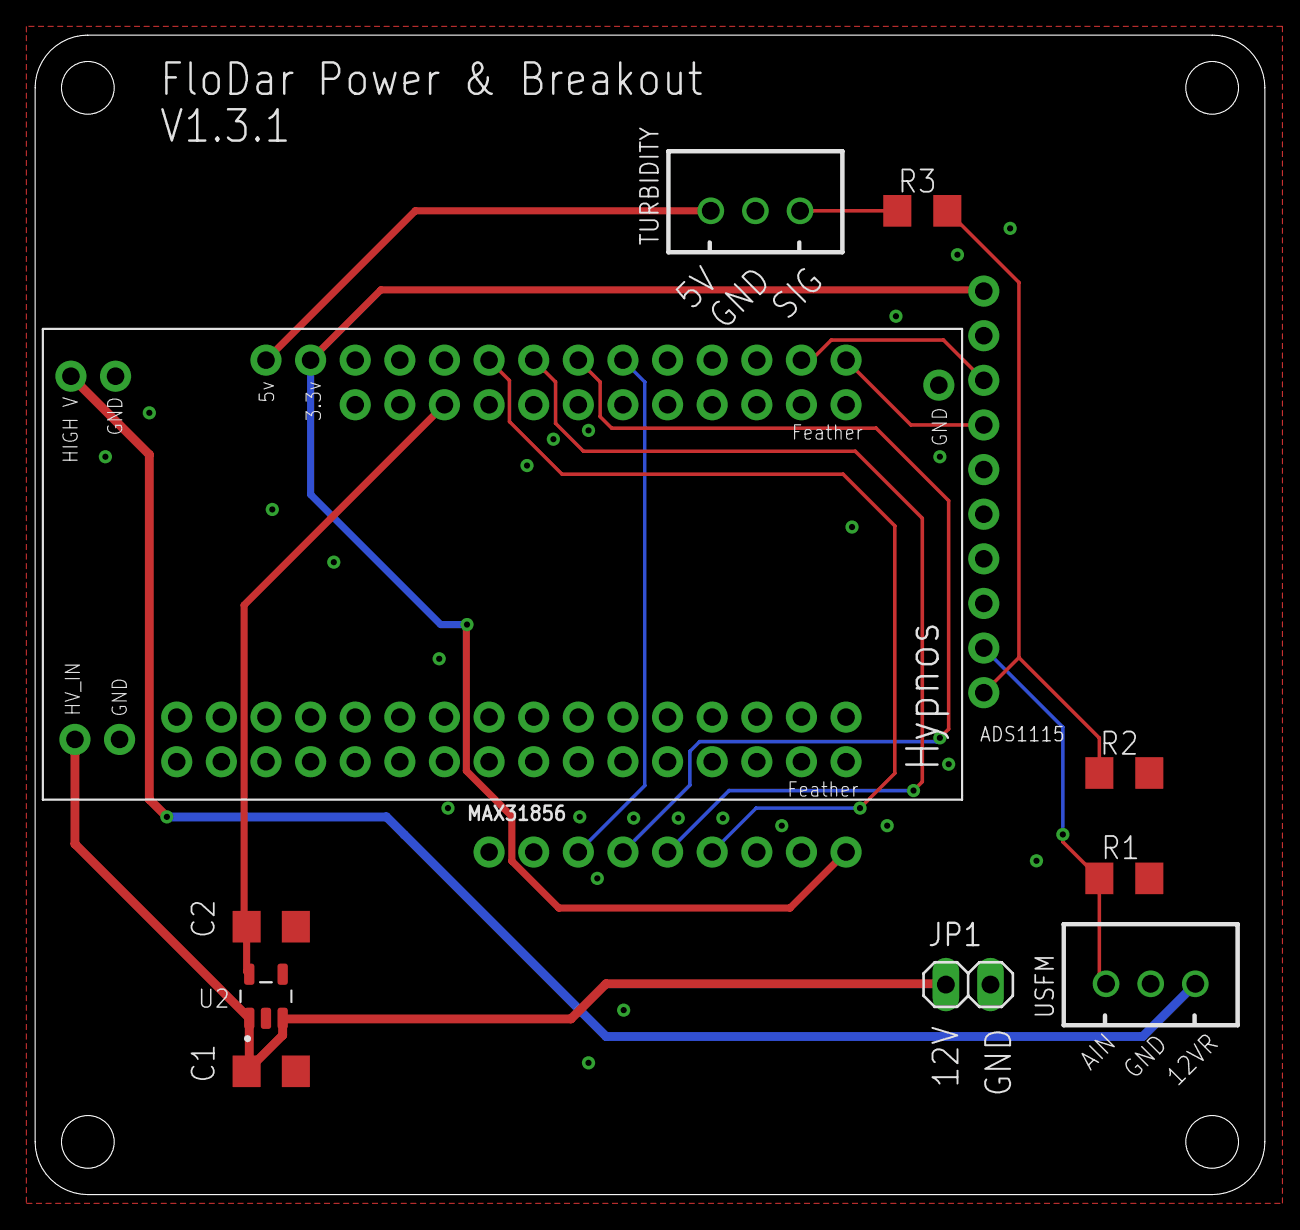
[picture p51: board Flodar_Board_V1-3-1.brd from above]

Board: 2 copper layers, 70.0 x 66.0 mm, 12 parts (0 on the bottom side), 15 nets.

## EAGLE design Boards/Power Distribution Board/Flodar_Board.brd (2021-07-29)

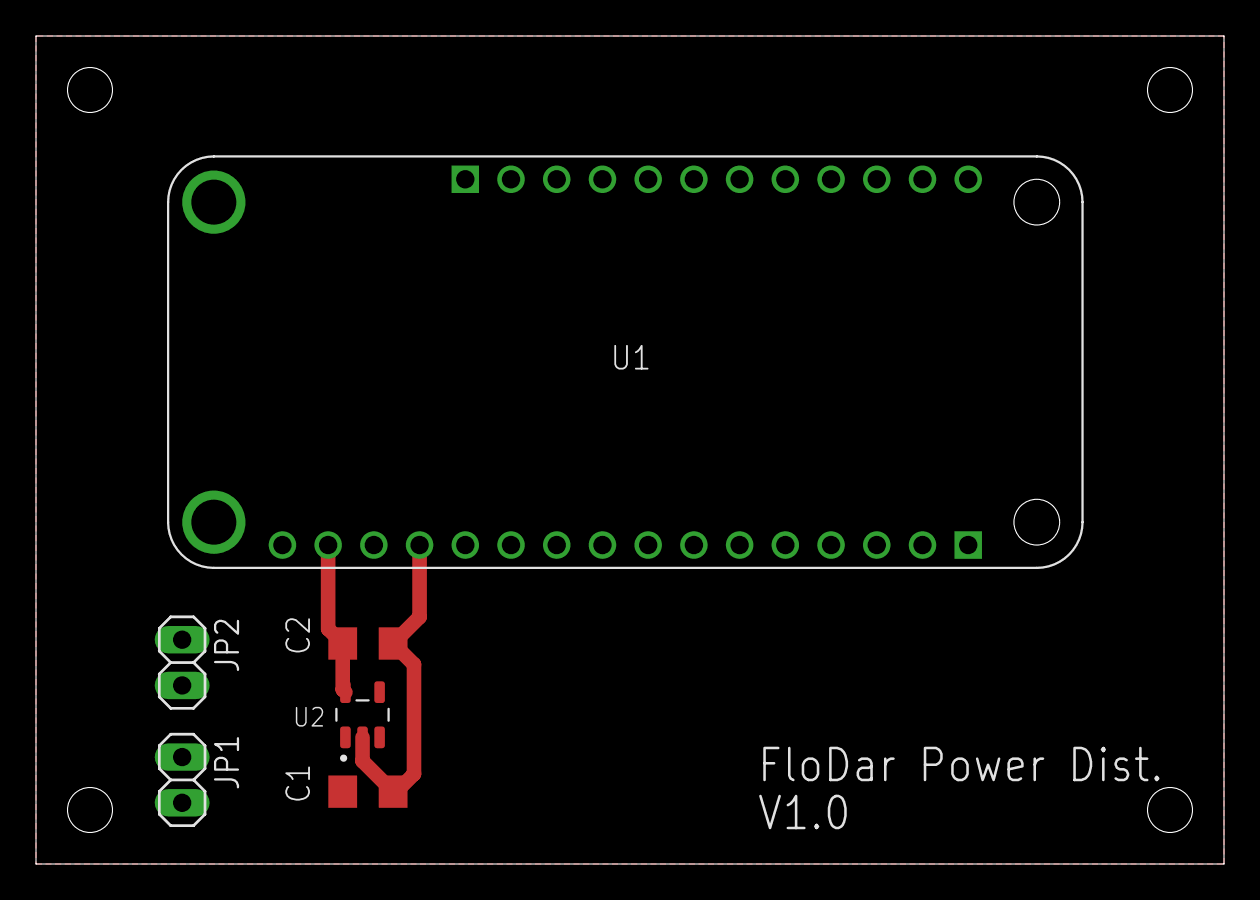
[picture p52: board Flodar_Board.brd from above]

Board: 2 copper layers, 66.0 x 46.0 mm, 6 parts (0 on the bottom side), 3 nets.

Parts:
C1: 1uF; C1206
C2: 3.3uF; C1206
JP1, JP2: 1X02
U1: FEATHER_M0_BASIC_PROTO; MODULE_FEATHER_M0_BASIC_PROTO
U2: LP2981-33DBVR; SOT95P280X145-5N

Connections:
3.3V: C2.1, U1.P1_15, U2.5
12V: C1.1, JP1.1, JP2.1, U2.1, U2.3
GND: C1.2, C2.2, JP1.2, JP2.2, U1.P1_1, U1.P1_13, U2.2

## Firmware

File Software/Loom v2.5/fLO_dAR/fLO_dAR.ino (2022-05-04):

///////////////////////////////////////////////////////////////////////////////

// This is a basic example that demonstrates usage of the Hypnos board
// Deep sleep functionality.

// The Hypnos board includes
// - SD
// - DS3231 RTC
// - Ability to power of peripherals

// Further details about the Hypnos board can be found here:
// https://github.com/OPEnSLab-OSU/OPEnS-Lab-Home/wiki/Hypnos

///////////////////////////////////////////////////////////////////////////////

#include <Loom.h>
// int Flow,Turbidity; 
// Include configuration
const char* json_config = 
#include "config.h"
;

// Set enabled modules
LoomFactory<
	Enable::Internet::Disabled,
	Enable::Sensors::Enabled,
	Enable::Radios::Enabled,
	Enable::Actuators::Enabled,
	Enable::Max::Enabled
> ModuleFactory{};

LoomManager Loom{ &ModuleFactory };

volatile bool rtc_flag = false;

void wakeISR_RTC() {
	// disable the interrupt
	detachInterrupt(12);
	rtc_flag = true;
}

void setup() 
{
	// Needs to be done for Hypno Board
	pinMode(5, OUTPUT);		// Enable control of 3.3V rail 
	pinMode(6, OUTPUT);		// Enable control of 5V rail 
	pinMode(12, INPUT_PULLUP);		// Enable waiting for RTC interrupt, MUST use a pullup since signal is active low
  pinMode(13, OUTPUT);

	//See Above
	digitalWrite(5, LOW);	// Enable 3.3V rail
	digitalWrite(6, HIGH);	// Enable 5V rail
  digitalWrite(13, LOW);

	Loom.begin_serial(true);
	Loom.parse_config(json_config);
	Loom.print_config();

	// Register an interrupt on the RTC alarm pin
	Loom.InterruptManager().register_ISR(12, wakeISR_RTC, LOW, ISR_Type::IMMEDIATE);

	LPrintln("\n ** Setup Complete ** ");
	Serial.flush();
}


void loop() 
{
	digitalWrite(5, LOW); // Enable 3.3V rail
  digitalWrite(6, HIGH);  // Enable 5V rail
  digitalWrite(13, HIGH);
  digitalWrite(LED_BUILTIN, HIGH);
	// As it turns out, if the SD card is initialized and you change
	// the states of the pins to ANY VALUE, the SD card will fail to
	// write. As a result, we ensure that the board has been turned
	// off at least once before we make any changes to the pin states
	if (rtc_flag) {
		pinMode(23, OUTPUT);
		pinMode(24, OUTPUT);
		pinMode(10, OUTPUT);

    // delay(1000);

		Loom.power_up();
	}
  delay(10000);
	Loom.measure();
	Loom.package();
  //Flow = Loom.get_data_as(LoomModule(),ADS1115);
  //Turbidity = Loom.get_data_as(ADS1115,analog2);
	Loom.display_data();

	Loom.SDCARD().log();

	// set the RTC alarm to a duration of 10 seconds with TimeSpan
	Loom.InterruptManager().RTC_alarm_duration(TimeSpan(0,0,15,0));
	Loom.InterruptManager().reconnect_interrupt(12);

  digitalWrite(13, LOW);
	digitalWrite(5, HIGH); // Disable 3.3V rail
	digitalWrite(6, LOW);  // Disable 5V rail
	pinMode(23, INPUT);
	pinMode(24, INPUT);
	pinMode(10, INPUT);
  digitalWrite(LED_BUILTIN, LOW);
	// Sleep Manager autmatically calls power_down on every sensor before sleeping
	// And power_up after waking.

  rtc_flag = false;
	Loom.SleepManager().sleep();
	while (!rtc_flag);
}

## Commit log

2021-02-16 Upload Borads
    [FLODAR_V3.brd, FLODAR_V3.sch]
2021-02-16 Upload Arduino Sketch
2021-06-06 Update Circuit Diagrams
2021-06-06 Power Budget Diagram
2021-07-29 Add Power Dist. Board
    [FLODAR_V3.brd, FLODAR_V3.sch, Flodar_Board.brd, Flodar_Board.sch]
2021-07-30 Update Power Dist. Board
2021-08-19 Combine Breakout and Power Dist. Boards
    [FLODAR_V3.brd, FLODAR_V3.sch, Flodar_Board.sch, Flodar_Board_V1-1.brd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]
2021-08-24 Add Labels to Pins
    [Flodar_Board_V1-1.brd]
2021-08-31 Fix Board Dimention
    [Flodar_Board_V1-1.brd]
2021-09-28 Upload V1-2
    [Flodar_Board_V1-1.brd, Flodar_Board_V1-1.sch, Flodar_Board_V1-2.brd, Flodar_Board_V1-2.sch]
2021-09-28 Update Board V1-2
    [Flodar_Board_V1-2.brd, Flodar_Board_V1-2.sch]
2021-09-28 Update Circuit Diagram
2021-09-30 Upload Summer Data
    [FloDar Summer 2021 Deployment.xlsx]
2021-10-01 Upload Board V1.3.x
    [Flodar_Board_V1-3-1.brd, Flodar_Board_V1-3-1.sch]
2021-10-01 Pelican Structure CAD
    [1150 new case Base.SLDPRT, 1150 new case top.SLDPRT, 7310K11_Plastic Submersible Cord Grip.SLDPRT, 90695A033_Steel Thin Hex Nut.SLDPRT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]
2022-02-26 Update Circuit Diagram PNG
2022-04-20 Create FloDar FMEA.xlsx
    [FloDar FMEA.xlsx]
2022-07-14 Disable MAX31856
    MAX31856 is currently unused
2022-07-14 Update FloDar.ino
    Add battery voltage reading and logging
2022-07-14 Update FloDar_10sec.ino
    Add battery voltage read and log
2022-07-14 Update FloDar_30sec.ino
    Add battery voltage and logging
2022-10-14 Grouped solar board files and added gerber for current pcb
    [Flodar_Board_V1-1.brd, Flodar_Board_V1-1.sch, Flodar_Board_V1-2.brd, Flodar_Board_V1-2.sch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]
2023-03-30 Updated CAD files
    [1150 new case Base.SLDPRT, 1150 new case top.SLDPRT, 7310K11_Plastic Submersible Cord Grip.SLDPRT, 90695A033_Steel Thin Hex Nut.SLDPRT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]
2023-06-01 Updated insert files
    [FloDar_Insert_Solar_Turbidity_Print.stl, Flodar_Insert_Solar_Print.stl, Flodar_insert_2023-06-01.stl, Pelican_Structure_Print.stl]
2023-06-05 Updated insert for battery slot
    [FloDar_insert.stl, Flodar_insert_2023-06-01.stl]
2023-09-25 Added BOM and build guide
    [FloDar BoM Final.xlsx]

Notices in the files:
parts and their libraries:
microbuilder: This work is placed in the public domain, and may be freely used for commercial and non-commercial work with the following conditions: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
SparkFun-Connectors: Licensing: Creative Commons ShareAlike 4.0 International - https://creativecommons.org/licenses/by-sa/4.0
